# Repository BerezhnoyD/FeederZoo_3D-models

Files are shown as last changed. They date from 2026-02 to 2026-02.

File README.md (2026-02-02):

# FeederZoo_3D-models
Repository containing most of my 3d-printed models classified by their function
Contains my OpenSourceOpenField and a bunch of other stuff including the whole FeederZoo (multiple rodent feeders over the years)

Contents:
- BrainSurgery models
- FeederZoo models (lots of stuff here)
- OpenSourceLabEquipment (various models from various places)
- OpenSourceOpenField
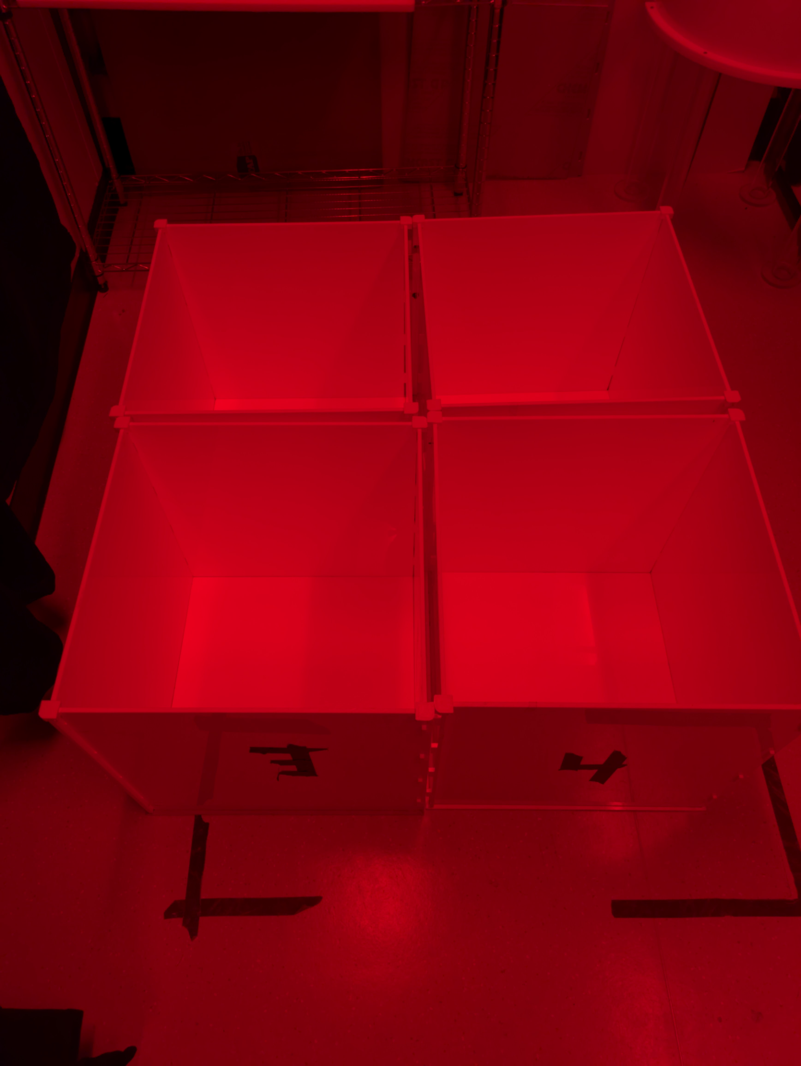
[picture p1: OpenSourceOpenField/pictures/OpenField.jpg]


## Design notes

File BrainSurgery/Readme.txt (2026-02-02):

This folder contains all the model files related
to stereotactic surgery and implants.
- Mouse headlplate files
- Holders compatible with Thorlabs poles to headfix mice with headplates/titanium bars
- Simple motorized addon for the RWD stereotax (motor housing, gear and board housing)
- Simple Cap/Shaft for Neuronexus silicon probes, tested with 32channel probes

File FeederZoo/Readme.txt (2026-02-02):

This folder contains the Whole zoo of animal feeders used
in my various behavioral projects over the years. Feel free to explore 
and modify to your needs.
- FED feeder (slightly modified pellet hopper from Markowitz lab/ eventually turned into a disc hopper for ReachOut)
- Homecage_Feeder (copied from another repository, used as an inspiration for own systems)
- ReachOut disc feeder (disc feeder used for out project with motor kinematics, see ReachOut repo or article)
- Ohanes_DIY_Linear_Servo (linear actuator turned precision pellet delivery system by my friend at VAI)
- Operant_Camera MIPT (operant camera and a feeder developed by my friends at MIPT)
- Water_delivery (syringe pump models used for my head-fixed reaching setup, see ReachOut repo)

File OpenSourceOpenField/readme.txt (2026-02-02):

This repository includes all the designs to make a module open-field box
40x40cm in size using the 5mm Acrylic Sheets.

Instructions:
For one Open field you will need to cut 5 Acrylic sheets and print 4 corners to
hold them together

1. Using the Laser Cutter (we used VLS 4.60 Laser Cutter) cut 4 side walls using 
the Illustrator files provided (Open field box-wall.ai). All walls are cut using
the same design and are hold together by the slots/spikes on the opposite side,
making all of them interchangeable. 
Use white acrylic sheets (3mm thickness) for the walls and don't remove the protective paper, 
otherwise the laser will leave the black burned marks on the surface.

2. Using the Laser Cutter cut the groves in a 5mm acryllic sheet to use it as an open-field
base. Groves are needed to hold 4 walls in place and should be at least 2-3mm deep, the deeper
the better. Provided Illustrator file (Open field box-bottom.ai) has only one grove (in grey)
as we have found that simply engraving one at a time and then rotating the sheet manually takes
much less time then engraving all. You might also want to experiment with the speed of the laser
cutter to make the grove deeper, or make some adjustments to the design

3. Using the PLA 3d printer and provided design (Open field box-corner.stl) print 4 corners to hold
the walls together. The open field can be used even without the corners due to its design,
but they add additional stability.

4. Assemble the parts in place - put the base on the floor, insert 4 walls into each other (spikes into
slots) and the base, and finish with putting 4 corners on top. The open field is ready for your experiments.
To wipe the base after the experiment you can simply lift 4 walls and then put them back in place.

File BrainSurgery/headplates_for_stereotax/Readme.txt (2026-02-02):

This folder contains all the files used for fabrication of 
titanium headplates for mouse surgeries. We printed the them using
SendCutSend service and 3mm titanium, 
but you can find another service/material of your choice.

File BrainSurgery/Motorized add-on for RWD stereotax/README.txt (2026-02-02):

Motorized add-on for RWD stereotaxic instruments by Remi-Rafael on Thingiverse: https://www.thingiverse.com/thing:7032259

Summary:
This design is an add on to motorize a RWD stereotaxic manual instrument and drive it with a servomotor. I designed it to allow slow and regular probe insertions.It adapts to the stereotaxic arm, holds with two screws and can be easily removed. The motor can be engaged or disengaged for manual control using a knob. I used 2 servo-tester modules to make a control board. The 3D parts and schematics are included.Different gears are included depending on the reduction ration you need.The servo teste i use can be found here https://www.amazon.com/GoolRC-Tester-Consistency-Helicopter-Airplane/dp/B00LTOD4F4 (and cheaper on aliexpress)

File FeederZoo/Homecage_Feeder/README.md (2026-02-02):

# **Overview**:

This system allows the user to host up to 5 mice in their home environment and automatically administer the single pellet reaching test to those animals. The system can run unsupervised and continuously for weeks at a time, allowing all 5 mice to perform an unlimited number of single pellet trials at their leisure. 

The design allows a single mouse at a time to enter the reaching tube. Upon entry, the animal’s RFID tag will be read, and if authenticated, a session will start for that animal. A session is defined as everything that happens from the time an animal enters the reaching tube to when they leave the tube. At the start of a session, the animal’s profile will be read and the task difficulty as well as the left and right preference will be automatically adjusted by moving the pellet presentation arm to the appropriate distance both away from the reaching tube and from right to left. Pellets will continue to be presented periodically until the mouse leaves the tube, at which point the session will end. Video and other data is recorded for the duration of each session. At session end, all the data for the session is saved in an organized way. We also have an auxiliary function for counting the successful rate of displaying a pellet using MobileNetV2 based on tensorflow and keras.

For further analyse, you can check the repository posted here:
https://github.com/SilasiLab/HomecageSinglePellet_Manual

# **Dependencies:**
* Ubuntu v16.04 LTS: Kernel version 4.4.19-35 or later
* Or Windows 10 is recommended, since the backend camera driver performs better that the one on linux in our experiment.
* Anaconda 3 environment, for the dependancies without a version number, it means there is no specific requirement on it. 
	* Python==3.6.10
	* pySerial==3.4	
	* numpy==1.18.1
	* OpenCV=4.1.2 (A whl file is provided under requirment folder.)
	* tkinter=8.6.8
	* matplotlib=3.1.3
	* Pillow
	* tqdm
	* tensorflow=1.10.0
	* keras=2.2.4
	* psutil
	* multiprocessing
	* subprocess
	
* Arduino IDE v1.8.5

# **Software Installation:**
1. Windows 10 is strongly recommended for a better support of camera driver. Ubuntu 16.04 LTS is alternative.
2. Install Anaconda. (https://www.anaconda.com/distribution/)
3. Install Arduino IDE v1.8.5. (https://www.arduino.cc/en/Main/Software)
	
4. Create and configure a virtual environment for installing the HomeCageSinglePellet code.
	- `conda create -n <yourenvname> python=3.6.10 anaconda`
	- `conda activate <yourenvname>`
	- `conda install -c anaconda numpy==1.18.1`
	- `conda install -c anaconda pyserial==3.4`
	- `conda install -c anaconda tk==8.6.8`
	- `conda install -c conda-forge matplotlib`
	- `conda install tqdm`
	- `conda install Pillow`
	- `conda install tensorflow==1.10.0`
	- `conda install keras==2.2.4`
	- `pip install psutil`
	- `pip install /path/to/HomeCageSinglePellet_server/requirment/opencv_python-4.1.2+contrib-cp36-cp36m-win_amd64.whl`

5. `git clone https://github.com/SilasiLab/HomeCageSinglePellet_server.git`

# **Assembly:**

The detailed assembly manual can be found here:
https://github.com/SilasiLab/HomeCageSinglePellet_server/blob/master/Homecage%20assembly%20manual.pdf

# **Usage**:
### **Running the Device**
1. Enter the virtual environment that the system was installed in by typing `conda activate <my_env>` into a terminal.

2. Optional: Use `cd` to navigate to` HomeCageSinglePellet_server/src/client/` and then run `python -B genProfiles.py`. The text prompts will walk you through entering your new animals into the system. Since the folder and the file are already inclued in this repo, this step is optional.

3. Open HomeCageSinglePellet_server/config/config.txt and set the system configuration you want.

4. Find the COM port ids for Arduino and RFID reader, using `mode` command in terminal.
(In linux: Arduino needs to be USB0 , and RFID reader needs to be USB1. You can see connected USB devices with terminal command:
ls /dev/tty* and You need to replace the COMs in main.py -> `sys_init()` function manually.) 
  
5. Open a termanal and run following command:
* `cd \your\path\to\HomeCageSinglePellet_server\src\client\`
* `conda activate YourEnvironment` replace YourEnvironment by the name of your environment.
* `python main.py COM-arduino COM-RFID` replace COM-arduino and COM-RFID by the COM ids of Arduino and RFID respectively.

6. Optional: If you have a google file stream mounted on this computer, you can choose to upload all the viedos and log files to google drive. You need firstly find out the local path to this google drive folder, in this case it is: `G:\Shared drives\SilasiLabGdrive`.
Since there could be mutiple cage running on the same computer and they can also be stored in the same google cloud folder. You can add a suffix to the project foler name by changing the root folder name from `HomeCageSinglePellet_server` to `HomeCageSinglePellet_server_id`(replace the id by your id) 
In the same folder, open another terminal and activate the virtual environment again, modify the cage ID in the script googleDriveManager.py, then run `python googleDriveManager.py \path\to\your\cloud\drive\folder`.
The videos and the log files will be stored in `your cloud drive\homecage_id_sync`.

7. You need to put in the RFID tag numbers manually into the profiles. Take mouse 1 as an instance, you need to replace the first line in `HomeCageSinglePellet_server\AnimalProfiles\MOUSE1\MOUSE1_save.txt`. If you do not know your tag number, don't worry. You can scan it on the RFID reader, it will be printed in the Terminal as `[tag number] not recognized`.

8. To test that everything is running correctly, block the IR beam breaker with something
	and scan one of the system’s test tags. If a session starts properly, it’s working. You will also be able to find out hom many pellets have been succefully displayed out of current displays we have as it is shown in the terminal too. 

9. To shut the system down cleanly; 

	- Ensure no sessions are currently running. 
	- Press the quit button on the GUI.
	- Ctrl+c out of the program running in the terminal.

# **Troubleshooting**:

* Is everything plugged in?
* Make sure you are in the correct virtual environment.
* Make sure the HomeCageSinglePellet/config/config.txt file contains the correct configuration. (If the file gets deleted it will be replaced by a default version at system start)
* Make sure there are 1 to 5 profiles in the HomeCageSinglePellet/AnimalProfiles/ directory. Ensure these profiles contain all the appropriate files and that the save.txt file for each animal contains the correct information.

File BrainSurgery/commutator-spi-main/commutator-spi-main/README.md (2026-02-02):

# Torque-free SPI Commutator

The wide-spread availability of 6 degree of freedom pose tracking using internal-measurement units
(IMUs) allows continuous monitoring of an animal's rotational state in an environment. This obviates
the need for tether torque measurements to drive an active commutator since the rotational state of
the animal is known in real-time, and the commutator can simply follow along. This commutator
supports SPI tethers i.e. any headstage that connects to the [standard 12-conductor SPI
cables](https://intantech.com/RHD_SPI_cables.html) with Omnetics connectors.

Zero-torque coaxial commutator.

This commutator functions with headstages that can provide orientation data over SPI. It can also be
used with SPI headstages without an IMU, e.g. using video-based rotation tracking since its remote
control interface is agnostic to how rotational measurements are taken.

For more information, visit the [commutator docs](https://open-ephys.github.io/commutator-docs/).

## Bill of Materials (BOM)

The following BOM pertains to the commutator's mechanical design. You can find the electronics BOM in the [commutator-controller repo](https://github.com/open-ephys/commutator-controller/tree/main/pcb/manufacturing/bom).

| Qty. | Part | Part No. | Description | Link |
| --- | --- | --- | --- | --- |
| 1	| Slip Ring Rotary Joint | Custom part from Orbex | 12-channel Slip Ring with Omnetic Connectors | - |
| 1 | NEMA 11 motor | 11HS18-0674S | 45mm length, 1.8 deg step angle, ~600mA max | [link](https://www.omc-stepperonline.com/nema-11-bipolar-1-8deg-9-5ncm-13-5oz-in-0-67a-4-6v-28x28x45mm-4-wires-11hs18-0674s) |
| 1 | 3D printed case | Custom part | 3D printed | [link](https://github.com/open-ephys/commutator-spi/tree/main/mechanical/production) |
| 1 | 3D printed motor gear | Custom part | 3D printed | [link](https://github.com/open-ephys/commutator-spi/tree/main/mechanical/production) | 
| 1 | 3D printed commutator gear | Custom part | 3D printed | [link](https://github.com/open-ephys/commutator-spi/tree/main/mechanical/production) | 
| 3 | M5 x 8mm socket head cap screws | 91290A224 | for attaching rotary joint to case | [link](https://www.mcmaster.com/91290A224) |
| 4 | M2.5 x 8mm socket head cap screws | 91290A102 | for attaching motor to case | [link](https://www.mcmaster.com/91290A102) |
| 4 | M2.5 x 8mm button head screws | 91239A756 | for attaching PCB to the case | [link](https://www.mcmaster.com/91239A756) |
| 1 | Control PCB | - | - | [link](https://github.com/open-ephys/commutators/tree/main/pcb/manufacturing/gerber) |
| 1 | eBOM | - | electrical components for assembling the PCB | [link](https://github.com/open-ephys/commutators/blob/main/pcb/manufacturing/bom/oe-commutator-controller.html) |

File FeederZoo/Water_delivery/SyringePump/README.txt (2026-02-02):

Syringe Pump by Mapleperson on Thingiverse: https://www.thingiverse.com/thing:3695610

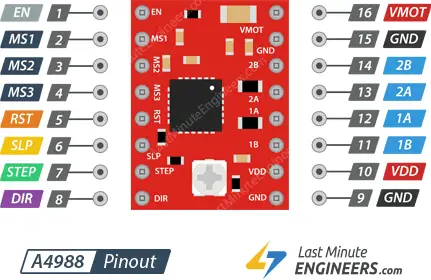
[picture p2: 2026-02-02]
BrainSurgery/Motorized-Commutator-main/Motorized-Commutator-main/Rx-PCB/Images/A4988-Stepper-Motor-Driver-Pinout.webp

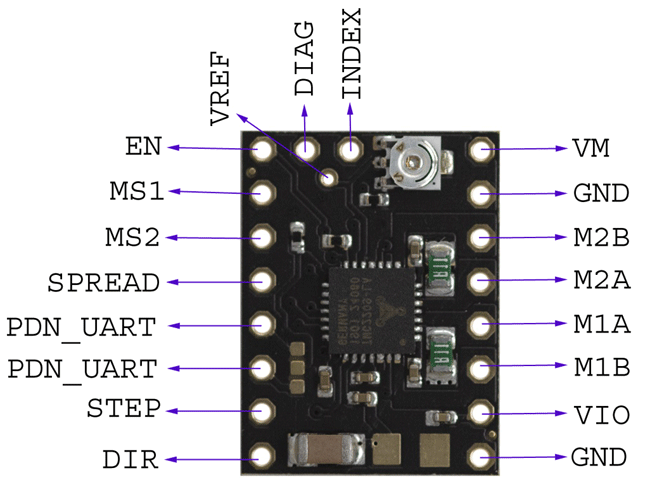
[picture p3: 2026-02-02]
BrainSurgery/Motorized-Commutator-main/Motorized-Commutator-main/Rx-PCB/Images/TMC2209-Stepper-Motor-Driver-Module-Pinout.png

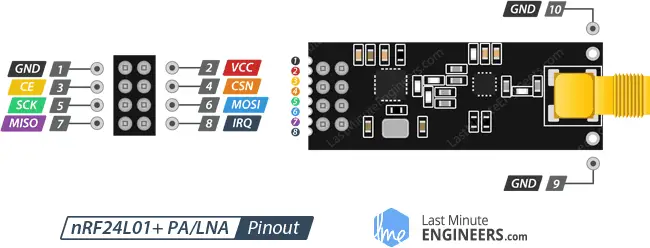
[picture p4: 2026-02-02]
BrainSurgery/Motorized-Commutator-main/Motorized-Commutator-main/Rx-PCB/Images/Pinout-nRF24L01-PA-LNA-External-Antenna-Wireless-Transceiver-Module.webp

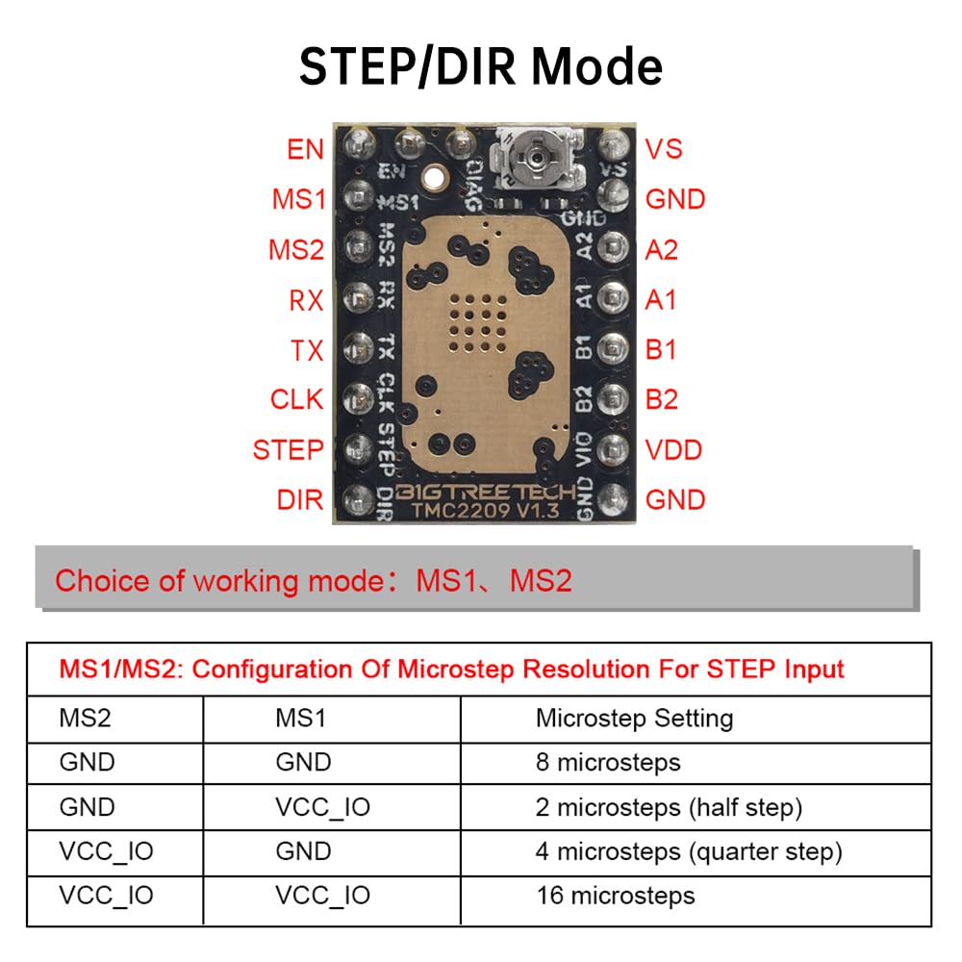
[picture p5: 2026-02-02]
BrainSurgery/Motorized-Commutator-main/Motorized-Commutator-main/Rx-PCB/Images/TMC2209_BIGTREE_Pinout.jpg

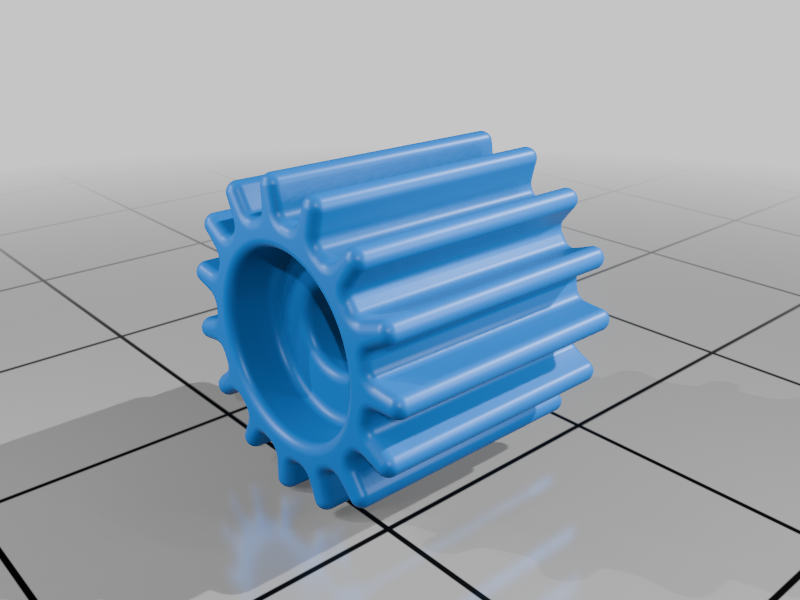
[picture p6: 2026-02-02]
BrainSurgery/Motorized add-on for RWD stereotax/images/Small_gear_1.png

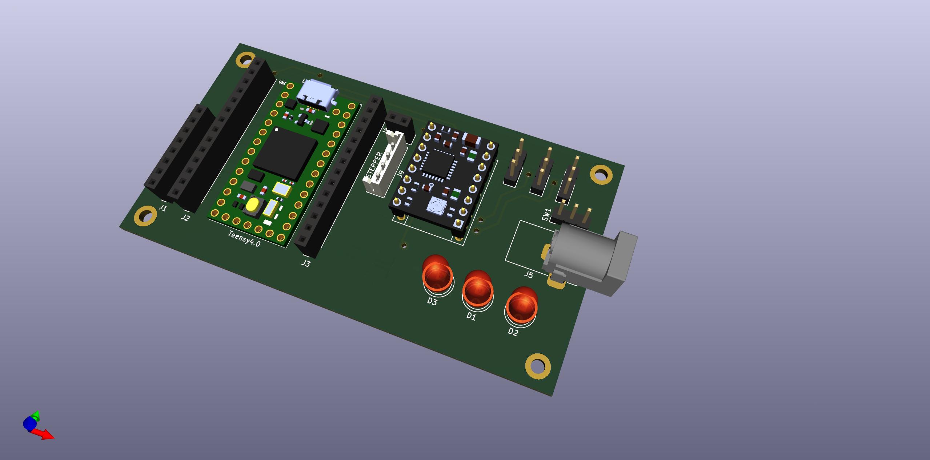
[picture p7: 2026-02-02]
BrainSurgery/Motorized-Commutator-main/Motorized-Commutator-main/Rx-PCB/Images/MC_Circuit_v2.jpg

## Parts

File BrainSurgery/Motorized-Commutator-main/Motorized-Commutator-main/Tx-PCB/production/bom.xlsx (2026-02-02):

Designator | Footprint | Quantity | Value | Manufacturer | Link
C1, C3 | 0805 | 2 | 4.7u | Digikey | https://www.digikey.com/short/3w5d9w2t
C2, C4, C5 | 0805 | 3 | 100n | Digikey | https://www.digikey.com/short/4dd80znh
C6 | 0805 | 1 | 10u | Digikey | https://www.digikey.com/short/wmr939bj
D1 | 1206 | 1 | Blue LED | Digikey | https://www.digikey.com/short/mf92djr0
D2 | 1206 | 1 | Red LED | Digikey | https://www.digikey.com/short/r8fdmfmb
J1 | PinSocket_2x04_P2.54mm_Vertical | 1 | NRF24L01 (Pin Sockets) | Digikey | https://www.digikey.com/short/vdjmc8hp | Amazon | https://a.co/d/cfL7IRG
J2 | PinSocket_1x10_P2.54mm_Vertical | 1 | Conn_01x10_Female | Digikey | https://www.digikey.com/short/pmj98dpn | Amazon | https://a.co/d/0p1lfKS
J3 | PinSocket_1x14_P2.54mm_Vertical | 1 | Conn_01x14_Female | Digikey | https://www.digikey.com/short/d7hpvht0 | Amazon | https://a.co/d/bVOCXlm
R1, R2 | 0805 | 2 | 220R | Digikey | https://www.digikey.com/short/1dt4nj9j
S1 | SW_100SP1T1B4M2QE | 1 | SW_SPDT_MODE | Digikey | https://www.digikey.com/short/8rz9r7b4
U1 | XDCR_COM-09032 | 1 | LEFT_STICK | Digikey | https://www.digikey.com/short/4ddjt05h
U2 | MODULE_DEV-15583 | 1 | Teensy4.0 (Pin Sockets) | Amazon | https://a.co/d/bVOCXlm
U3 | SOT-223-3_TabPin2 | 1 | LD1117S33TR_SOT223 | Digikey | https://www.digikey.com/short/zf93pn3w
U4 | XDCR_COM-09032 | 1 | RIGHT_STICK | Digikey | https://www.digikey.com/short/4ddjt05h
 | JUMPER |  |  | Digikey | https://www.digikey.com/short/t05tvr0v
 | Pin Headers Male |  |  | Digikey | https://www.digikey.com/short/n5mf5ppp
 | LD1117S50TR |  |  | Digikey | https://www.digikey.com/short/v05bp89n
 | Green LED |  |  | Digikey | https://www.digikey.com/short/2q5jbftb
 | 1.27mm Pin Header |  |  | Digikey | https://www.digikey.com/short/jfpnqzmq
 | 100u |  |  | Digikey | https://www.digikey.com/short/7h7q48zm
 | Barrel Jack |  |  | Digikey | https://www.digikey.com/short/df3m72bh
 | Teensy 4.0 |  |  | Digikey | https://www.digikey.com/short/wq508nbr
 | Teensy 4.0 (Headers) |  |  | Digikey | https://www.digikey.com/short/jrw35j00
 | NRF24L01 |  |  | Digikey | https://www.digikey.com/short/q3cj1zqz | Amazon | https://a.co/d/0G7uEZj
 | TMC2209 |  |  | Digikey | https://www.digikey.com/short/c970td25 | Amazon | https://a.co/d/i0fe6RV

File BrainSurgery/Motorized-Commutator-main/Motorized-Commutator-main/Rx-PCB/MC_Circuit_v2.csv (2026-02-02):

Item | Qty | Reference(s) | Value | LibPart | Footprint | Ordered or Available | Datasheet | MANUFACTURER | MAXIMUM_PACKAGE_HEIGHT | STANDARD
 |  | A1 | Pololu_Breakout_A4988 | Driver_Motor:Pololu_Breakout_A4988 | Module:Pololu_Breakout-16_15.2x20.3mm | Yes | https://www.pololu.com/product/2980/pictures
 |  | C1 | 4.7u | Device:C_Polarized_Small | Capacitor_SMD:C_0805_2012Metric_Pad1.18x1.45mm_HandSolder |  | ~
 |  | C2 | 4.7u | Device:C_Polarized_Small | Capacitor_SMD:C_0805_2012Metric_Pad1.18x1.45mm_HandSolder |  | ~
 |  | C3 | 100n | Device:C_Small | Capacitor_SMD:C_0805_2012Metric_Pad1.18x1.45mm_HandSolder | Yes | ~
 |  | C4 | 100n | Device:C_Small | Capacitor_SMD:C_0805_2012Metric_Pad1.18x1.45mm_HandSolder | Yes | ~
 |  | C5 | 100n | Device:C_Small | Capacitor_SMD:C_0805_2012Metric_Pad1.18x1.45mm_HandSolder | Yes | ~
 |  | C6 | 10u | Device:C_Polarized_Small | Capacitor_SMD:C_0805_2012Metric_Pad1.18x1.45mm_HandSolder | Yes | ~
 |  | C7 | 100u | Device:C_Polarized | Capacitor_SMD:C_0805_2012Metric_Pad1.18x1.45mm_HandSolder |  | ~
 |  | D1 | MANUAL | Device:LED | LED_THT:LED_D5.0mm | Yes | ~
 |  | D2 | AUTO | Device:LED | LED_THT:LED_D5.0mm | Yes | ~
 |  | D3 | PWR IND | Device:LED | LED_THT:LED_D5.0mm | Yes | ~
 |  | D4 | MBR0520 | Diode:MBR0520 | Diode_SMD:D_SOD-123 |  | http://www.mccsemi.com/up_pdf/MBR0520~MBR0580(SOD123).pdf
 |  | J1 | NRF24L01 | Connector:Conn_01x08_Female | Connector_PinSocket_2.54mm:PinSocket_1x08_P2.54mm_Vertical | Yes | ~
 |  | J2 | Conn_01x14_Female | Connector:Conn_01x14_Female | Connector_PinSocket_2.54mm:PinSocket_1x14_P2.54mm_Vertical |  | ~
 |  | J3 | Conn_01x14_Female | Connector:Conn_01x14_Female | Connector_PinSocket_2.54mm:PinSocket_1x14_P2.54mm_Vertical |  | ~
 |  | J4 | 3.3V TAP | Connector:Conn_01x02_Female | Connector_PinSocket_2.54mm:PinSocket_1x02_P2.54mm_Vertical | Yes | ~
 |  | J5 | Barrel_Jack_MountingPin | Connector:Barrel_Jack_Switch | Connector_BarrelJack:BarrelJack_Horizontal |  | ~
 |  | J6 | MS1 | Connector:Conn_01x03_Male | Connector_PinHeader_2.54mm:PinHeader_1x03_P2.54mm_Vertical | Yes | ~
 |  | J7 | MS2 | Connector:Conn_01x03_Male | Connector_PinHeader_2.54mm:PinHeader_1x03_P2.54mm_Vertical | Yes | ~
 |  | J8 | MS3 | Connector:Conn_01x03_Male | Connector_PinHeader_2.54mm:PinHeader_1x03_P2.54mm_Vertical | Yes | ~
 |  | J9 | STEPPER | Connector:Conn_01x04_Female | Connector_JST:JST_EH_B4B-EH-A_1x04_P2.50mm_Vertical |  | ~
 |  | R1 | 330R | Device:R | Resistor_SMD:R_0805_2012Metric_Pad1.20x1.40mm_HandSolder | Yes | ~
 |  | R2 | 330R | Device:R | Resistor_SMD:R_0805_2012Metric_Pad1.20x1.40mm_HandSolder | Yes | ~
 |  | R3 | 330R | Device:R | Resistor_SMD:R_0805_2012Metric_Pad1.20x1.40mm_HandSolder | Yes | ~
 |  | SW1 | SW_SPDT | Switch:SW_SPDT | Connector_PinHeader_2.54mm:PinHeader_1x03_P2.54mm_Vertical |  | ~
 |  | U1 | Teensy4.0 | Teensy 4.0:DEV-15583 | Teensy 4.0:MODULE_DEV-15583 |  |  | Sparkfun | 5.87mm | Manufacturer Recommendations
 |  | U2 | LD1117S50TR_SOT223 | Regulator_Linear:LD1117S50TR_SOT223 | Package_TO_SOT_SMD:SOT-223-3_TabPin2 |  | http://www.st.com/st-web-ui/static/active/en/resource/technical/document/datasheet/CD00000544.pdf
Collated Components:
Item | Qty | Reference(s) | Value | LibPart | Footprint |  | Datasheet | MANUFACTURER | MAXIMUM_PACKAGE_HEIGHT | STANDARD
1 | 1 | A1 | Pololu_Breakout_A4988 | Driver_Motor:Pololu_Breakout_A4988 | Module:Pololu_Breakout-16_15.2x20.3mm |  | https://www.pololu.com/product/2980/pictures
2 | 2 | C1, C2 | 4.7u | Device:C_Polarized_Small | Capacitor_SMD:C_0805_2012Metric_Pad1.18x1.45mm_HandSolder |  | ~
3 | 3 | C3, C4, C5 | 100n | Device:C_Small | Capacitor_SMD:C_0805_2012Metric_Pad1.18x1.45mm_HandSolder |  | ~
4 | 1 | C6 | 10u | Device:C_Polarized_Small | Capacitor_SMD:C_0805_2012Metric_Pad1.18x1.45mm_HandSolder |  | ~
5 | 1 | C7 | 100u | Device:C_Polarized | Capacitor_SMD:C_0805_2012Metric_Pad1.18x1.45mm_HandSolder |  | ~
6 | 1 | D1 | MANUAL | Device:LED | LED_THT:LED_D5.0mm |  | ~
7 | 1 | D2 | AUTO | Device:LED | LED_THT:LED_D5.0mm |  | ~
8 | 1 | D3 | PWR IND | Device:LED | LED_THT:LED_D5.0mm |  | ~
9 | 1 | D4 | MBR0520 | Diode:MBR0520 | Diode_SMD:D_SOD-123 |  | http://www.mccsemi.com/up_pdf/MBR0520~MBR0580(SOD123).pdf
10 | 1 | J1 | NRF24L01 | Connector:Conn_01x08_Female | Connector_PinSocket_2.54mm:PinSocket_1x08_P2.54mm_Vertical |  | ~
11 | 2 | J2, J3 | Conn_01x14_Female | Connector:Conn_01x14_Female | Connector_PinSocket_2.54mm:PinSocket_1x14_P2.54mm_Vertical |  | ~
12 | 1 | J4 | 3.3V TAP | Connector:Conn_01x02_Female | Connector_PinSocket_2.54mm:PinSocket_1x02_P2.54mm_Vertical |  | ~
13 | 1 | J5 | Barrel_Jack_MountingPin | Connector:Barrel_Jack_Switch | Connector_BarrelJack:BarrelJack_Horizontal |  | ~
14 | 1 | J6 | MS1 | Connector:Conn_01x03_Male | Connector_PinHeader_2.54mm:PinHeader_1x03_P2.54mm_Vertical |  | ~
15 | 1 | J7 | MS2 | Connector:Conn_01x03_Male | Connector_PinHeader_2.54mm:PinHeader_1x03_P2.54mm_Vertical |  | ~
16 | 1 | J8 | MS3 | Connector:Conn_01x03_Male | Connector_PinHeader_2.54mm:PinHeader_1x03_P2.54mm_Vertical |  | ~
17 | 1 | J9 | STEPPER | Connector:Conn_01x04_Female | Connector_JST:JST_EH_B4B-EH-A_1x04_P2.50mm_Vertical |  | ~
18 | 3 | R1, R2, R3 | 330R | Device:R | Resistor_SMD:R_0805_2012Metric_Pad1.20x1.40mm_HandSolder |  | ~
19 | 1 | SW1 | SW_SPDT | Switch:SW_SPDT | Connector_PinHeader_2.54mm:PinHeader_1x03_P2.54mm_Vertical |  | ~
20 | 1 | U1 | Teensy4.0 | Teensy 4.0:DEV-15583 | Teensy 4.0:MODULE_DEV-15583 |  |  | Sparkfun | 5.87mm | Manufacturer Recommendations
21 | 1 | U2 | LD1117S50TR_SOT223 | Regulator_Linear:LD1117S50TR_SOT223 | Package_TO_SOT_SMD:SOT-223-3_TabPin2 |  | http://www.st.com/st-web-ui/static/active/en/resource/technical/document/datasheet/CD00000544.pdf

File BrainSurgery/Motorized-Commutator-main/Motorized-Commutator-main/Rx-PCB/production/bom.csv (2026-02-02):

Designator | Footprint | Quantity | Value | LCSC Part #
_3, _2, |  | 3
A1 | Pololu_A4988 | 1 | A4988/TMC2209
C1, C2 | 0805 | 2 | 4.7u
C3, C4, C5, C8 | 0805 | 4 | 100n
C6, C9 | 0805 | 2 | 10u
C7 | 0805 | 1 | 100u
D1 | 1206 | 1 | MANUAL
D2 | 1206 | 1 | AUTO
D3 | 1206 | 1 | PWR IND
J1 | PinSocket_2x04_P2.54mm_Vertical | 1 | NRF24L01
J10 | PinHeader_2x02_P2.54mm_Vertical | 1 | Conn_02x02_Odd_Even
J2 | PinSocket_1x10_P2.54mm_Vertical | 1 | Conn_01x10_Female
J3 | PinSocket_1x14_P2.54mm_Vertical | 1 | Conn_01x14_Female
J5 | BarrelJack_Horizontal | 1 | Barrel_Jack_MountingPin
J6 | PinHeader_1x03_P2.54mm_Vertical | 1 | MS1
J7 | PinHeader_1x03_P2.54mm_Vertical | 1 | MS2
J8 | PinHeader_1x03_P2.54mm_Vertical | 1 | MS3
J9 | JST_EH_B4B-EH-A_1x04_P2.50mm_Vertical | 1 | STEPPER
R1, R2, R3 | 0805 | 3 | 220R
S1 | SW_100SP1T1B4M2QE | 1 | SW_SPDT
U1 | MODULE_DEV-15583 | 1 | Teensy4.0
U2 | SOT-223-3_TabPin2 | 1 | LD1117S50TR_SOT223
U3 | SOT-223-3_TabPin2 | 1 | LD1117S33TR_SOT223

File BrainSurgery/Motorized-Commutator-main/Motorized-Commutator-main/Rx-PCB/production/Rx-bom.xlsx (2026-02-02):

Designator | Footprint | Quantity | Value | Manufacturer
_3, _2, |  | 3
A1 | Pololu_A4988 | 1 | A4988/TMC2209 | Digikey | https://www.digikey.com/short/c970td25 | Amazon | https://a.co/d/i0fe6RV
C1, C2 | 0805 | 2 | 4.7u | Digikey | https://www.digikey.com/short/3w5d9w2t
C3, C4, C5, C8 | 0805 | 4 | 100n | Digikey | https://www.digikey.com/short/4dd80znh
C6, C9 | 0805 | 2 | 10u | Digikey | https://www.digikey.com/short/wmr939bj
C7 | 0805 | 1 | 100u | Digikey | https://www.digikey.com/short/7h7q48zm
D1 | 1206 | 1 | MANUAL | Digikey | https://www.digikey.com/short/mf92djr0
D2 | 1206 | 1 | AUTO | Digikey | https://www.digikey.com/short/r8fdmfmb
D3 | 1206 | 1 | PWR IND | Digikey | https://www.digikey.com/short/2q5jbftb
J1 | PinSocket_2x04_P2.54mm_Vertical | 1 | NRF24L01 | Digikey | https://www.digikey.com/short/vdjmc8hp | Amazon | https://a.co/d/cfL7IRG
J10 | PinHeader_2x02_P2.54mm_Vertical | 1 | Conn_02x02_Odd_Even | Digikey | https://www.digikey.com/short/094vw344
J2 | PinSocket_1x10_P2.54mm_Vertical | 1 | Conn_01x10_Female | Digikey | https://www.digikey.com/short/pmj98dpn | Amazon | https://a.co/d/0p1lfKS
J3 | PinSocket_1x14_P2.54mm_Vertical | 1 | Conn_01x14_Female | Digikey | https://www.digikey.com/short/d7hpvht0 | Amazon | https://a.co/d/bVOCXlm
J5 | BarrelJack_Horizontal | 1 | Barrel_Jack_MountingPin | Digikey | https://www.digikey.com/short/df3m72bh
J6 | PinHeader_1x03_P2.54mm_Vertical | 1 | MS1 | Digikey | https://www.digikey.com/short/n5mf5ppp
J7 | PinHeader_1x03_P2.54mm_Vertical | 1 | MS2 | Digikey | https://www.digikey.com/short/n5mf5ppp
J8 | PinHeader_1x03_P2.54mm_Vertical | 1 | MS3 | Digikey | https://www.digikey.com/short/n5mf5ppp
J9 | JST_EH_B4B-EH-A_1x04_P2.50mm_Vertical | 1 | STEPPER | Digikey | https://www.digikey.com/short/0vr4phzf
R1, R2, R3 | 0805 | 3 | 220R | Digikey | https://www.digikey.com/short/1dt4nj9j
S1 | SW_100SP1T1B4M2QE | 1 | SW_SPDT | Digikey | https://www.digikey.com/short/8rz9r7b4
U1 | MODULE_DEV-15583 | 1 | Teensy4.0 | Digikey | https://www.digikey.com/short/jrw35j00
U2 | SOT-223-3_TabPin2 | 1 | LD1117S50TR_SOT223 | Digikey | https://www.digikey.com/short/v05bp89n
U3 | SOT-223-3_TabPin2 | 1 | LD1117S33TR_SOT223 | Digikey | https://www.digikey.com/short/zf93pn3w
 | JUMPER |  |  | Digikey | https://www.digikey.com/short/t05tvr0v

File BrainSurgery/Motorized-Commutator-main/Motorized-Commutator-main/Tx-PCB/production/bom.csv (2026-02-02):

Designator | Footprint | Quantity | Value | LCSC Part #
C1, C3 | 0805 | 2 | 4.7u
C2, C4, C5 | 0805 | 3 | 100n
C6 | 0805 | 1 | 10u
D1 | 1206 | 1 | MANUAL
D2 | 1206 | 1 | AUTO
J1 | PinSocket_2x04_P2.54mm_Vertical | 1 | NRF24L01
J2 | PinSocket_1x10_P2.54mm_Vertical | 1 | Conn_01x10_Female
J3 | PinSocket_1x14_P2.54mm_Vertical | 1 | Conn_01x14_Female
R1, R2 | 0805 | 2 | 220R
S1 | SW_100SP1T1B4M2QE | 1 | SW_SPDT_MODE
U1 | XDCR_COM-09032 | 1 | LEFT_STICK
U2 | MODULE_DEV-15583 | 1 | Teensy4.0
U3 | SOT-223-3_TabPin2 | 1 | LD1117S33TR_SOT223
U4 | XDCR_COM-09032 | 1 | RIGHT_STICK

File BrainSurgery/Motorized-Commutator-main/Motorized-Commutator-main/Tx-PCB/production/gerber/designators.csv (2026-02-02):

C1:1
C2:1
C3:1
C4:1
C5:1
C6:1
D1:1
D2:1
J1:1
J2:1
J3:1
R1:1
R2:1
S1:1
U1:1
U2:1
U3:1
U4:1

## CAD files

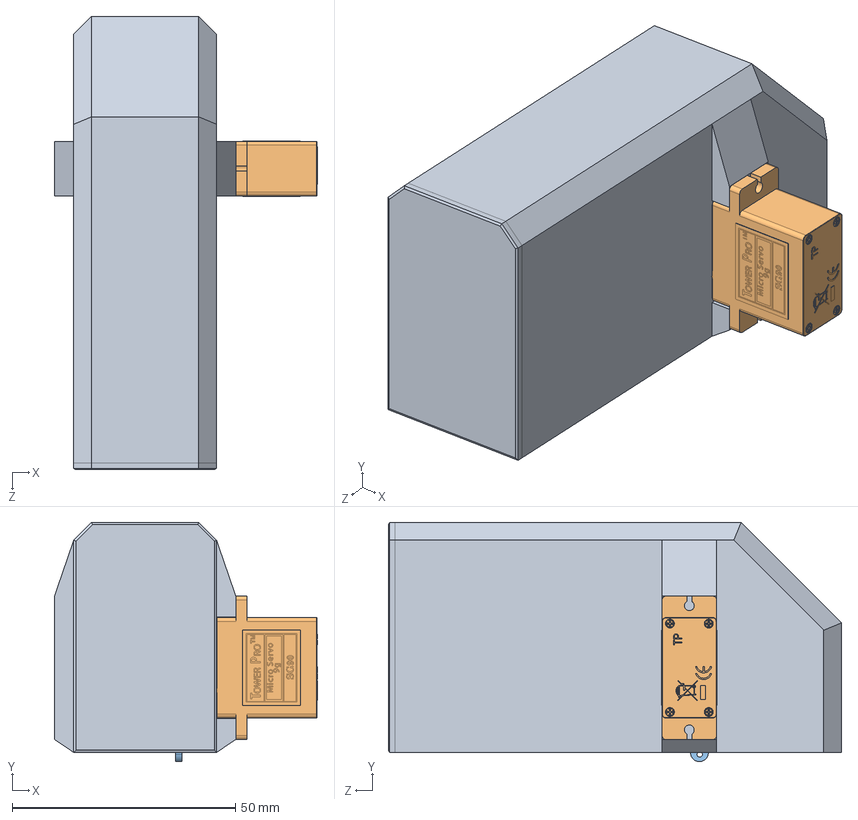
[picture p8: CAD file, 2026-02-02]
FeederZoo/Operant_Camera MIPT/Сборка1.SLDASM
58.9 x 53.6 x 101.5 mm
кормушка 2
SG90 - Micro Servo 9g - Tower Pro
SG90 - Micro Servo 9g - Tower Pro.3
вал

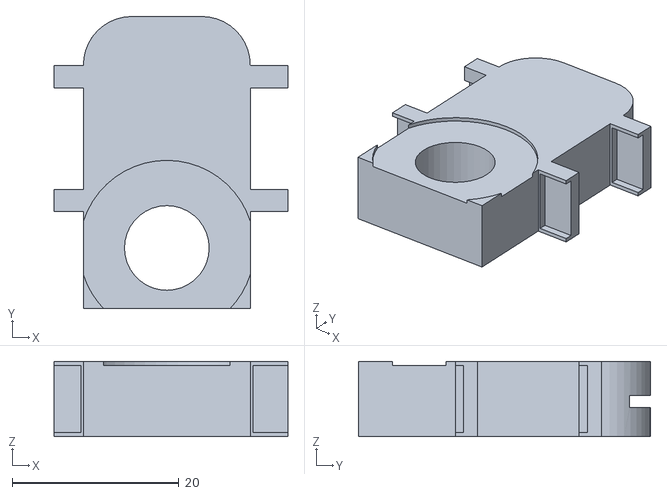
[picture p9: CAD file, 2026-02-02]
FeederZoo/Water_delivery/SyringePump/MouseParts/Mouse 2.0/Assembly Pump Mouse - M Carriage 1-2.STL
28.0 x 35.0 x 9.00

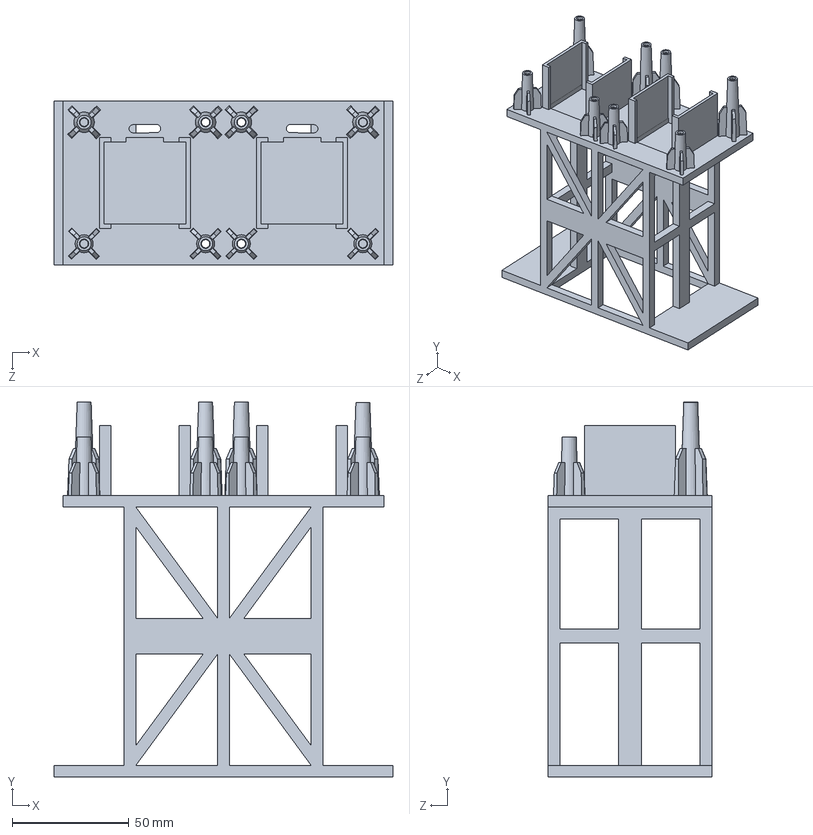
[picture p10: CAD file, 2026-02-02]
FeederZoo/Water_delivery/SyringePump/RatParts/Pho Combined Food Assembly - Skeleton - 15Matt.SLDPRT
145.0 x 160.5 x 70.0 mm

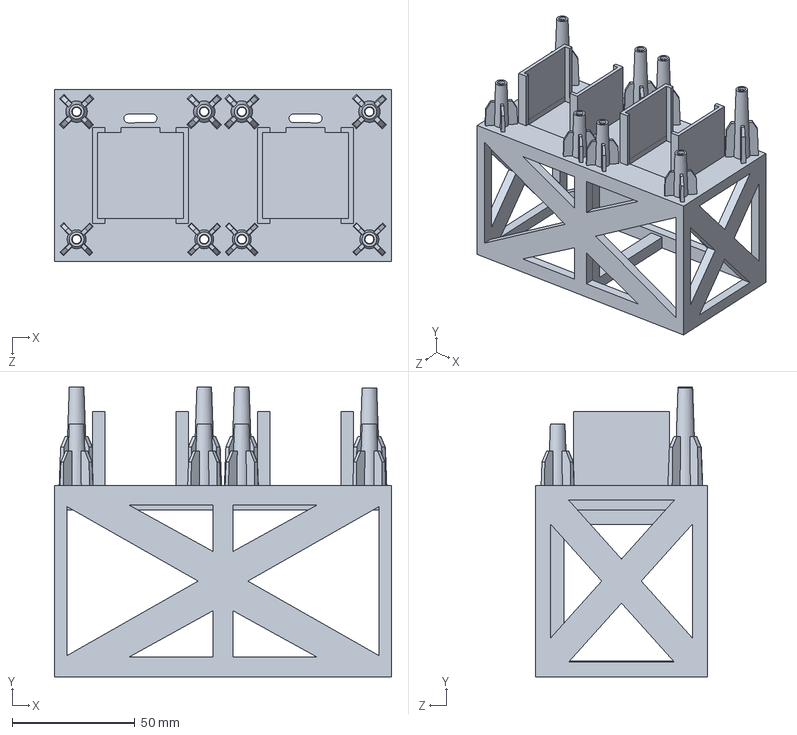
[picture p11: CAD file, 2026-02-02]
FeederZoo/Water_delivery/SyringePump/RatParts/Scaffolding/Pho Combined Food Assembly - Skeleton - 14.SLDPRT
137.3 x 118.0 x 70.0 mm

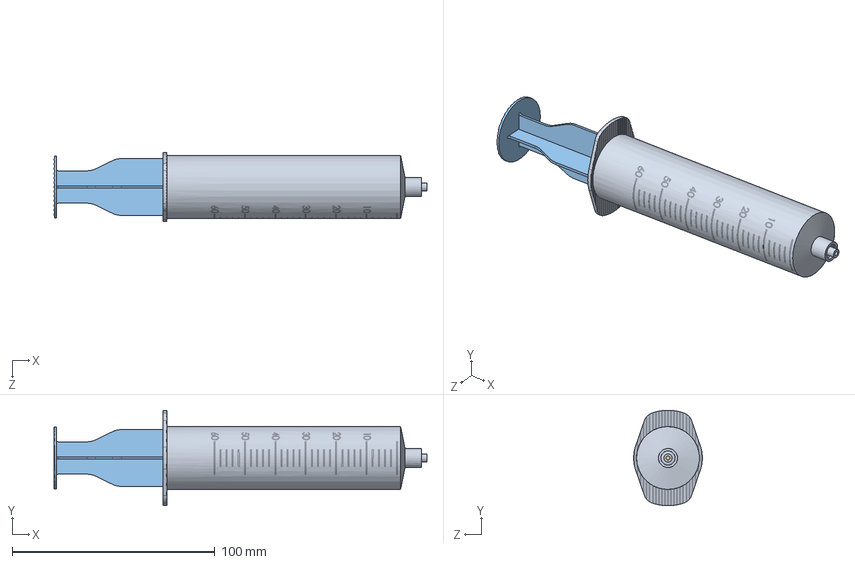
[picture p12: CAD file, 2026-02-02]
FeederZoo/Water_delivery/SyringePump/Syringe files/Syringe 60 ml.SLDASM
183.8 x 47.0 x 34.0 mm
Syringe_cylinder
Rubber tampon
Syringe_piston

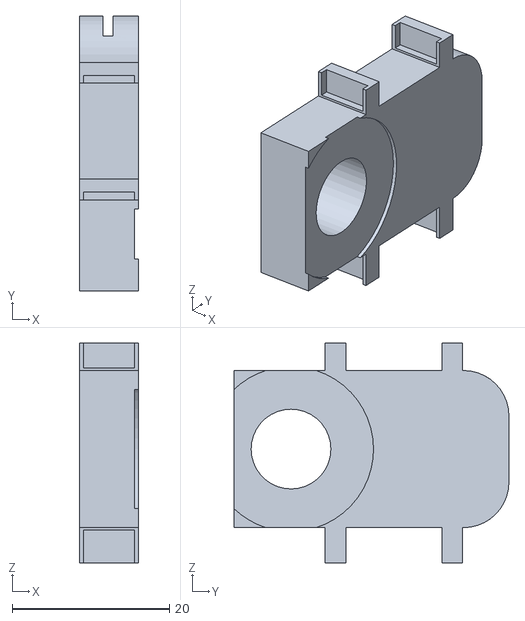
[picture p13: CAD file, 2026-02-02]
FeederZoo/Water_delivery/SyringePump/MouseParts/Mouse 2.0/Assembly Pump Mouse - M Carriage 1-1.STL
7.50 x 35.0 x 28.0

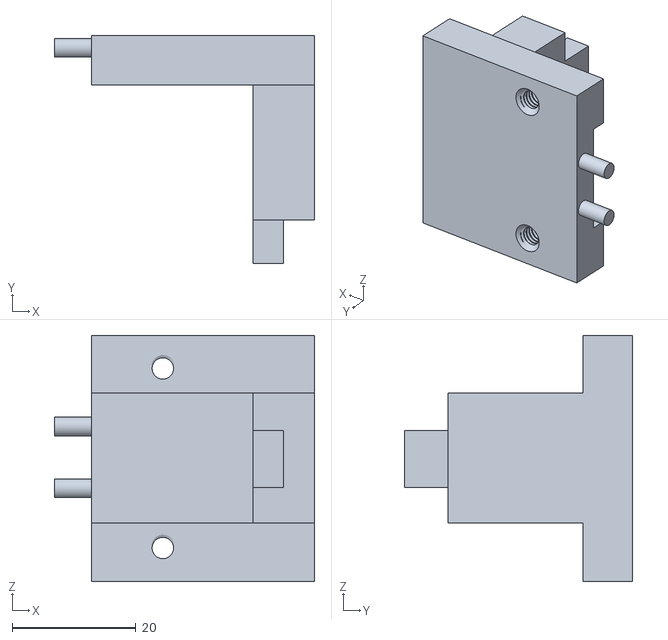
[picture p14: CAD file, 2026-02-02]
FeederZoo/Water_delivery/SyringePump/MouseParts/Mouse 2.0/Assembly Pump Mouse - M Top Lock-1.STL
42.0 x 36.9 x 39.8

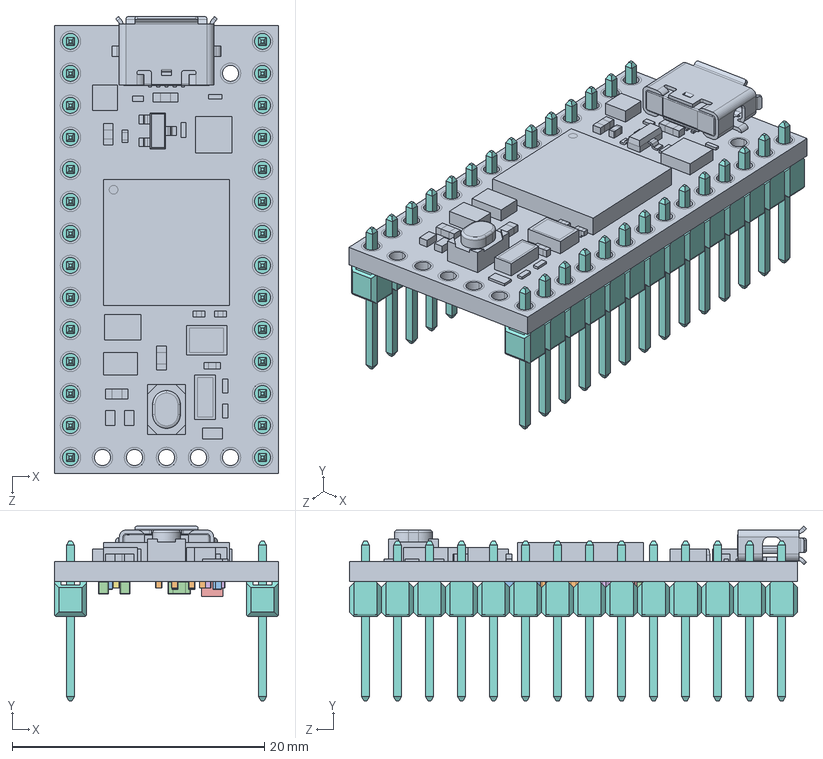
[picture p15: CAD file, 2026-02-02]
BrainSurgery/Motorized-Commutator-main/CAD/Motorized_Commutator/Teensy_40.SLDASM
17.8 x 13.9 x 36.3 mm
DEV-15583 board.step
C5-C18 (0.55mm).step
C20-C24 (0.65).step
R1-R3 (0.4inch)_1269AS-H-3R3M=P2.step
L1^DEV-15583 ASS.step
C.step x 2
C2.step
Pin Header 1x14 TH Pitch 2.54mm.stp x 2

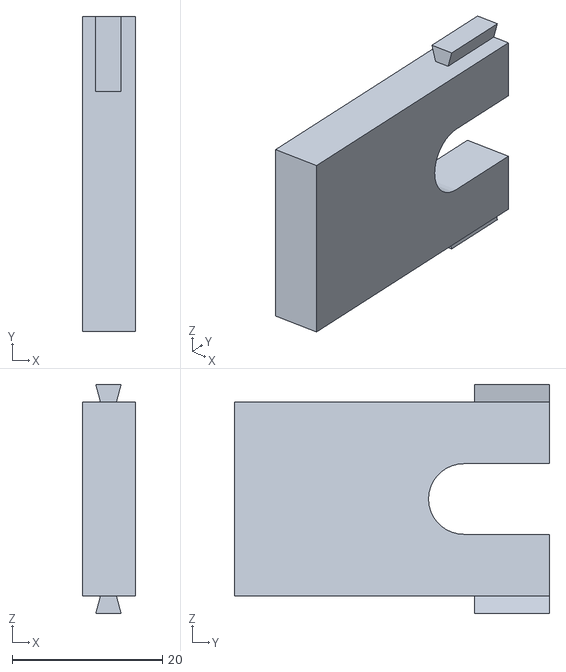
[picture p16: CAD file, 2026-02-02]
FeederZoo/Water_delivery/SyringePump/MouseParts/Mouse 2.0/Assembly Pump Mouse - M Front Face 1-1.STL
7.00 x 42.0 x 30.5

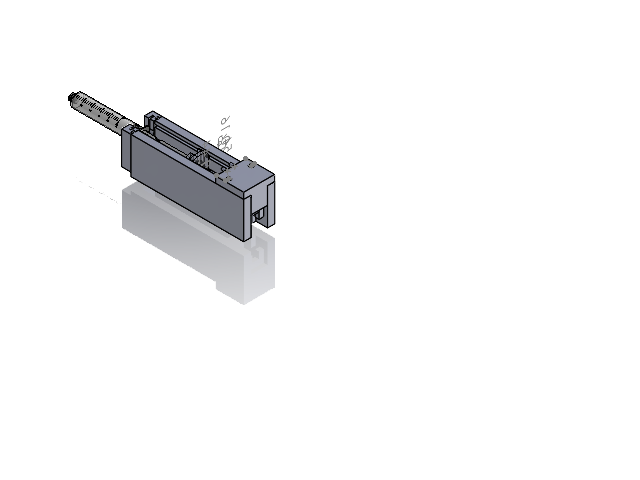
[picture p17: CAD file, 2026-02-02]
FeederZoo/Water_delivery/SyringePump/MouseParts/Assembly Pump Mouse.SLDASM
Syringe_cylinder_10ml
Rubber tampon_10ml
Syringe_piston_10ml
M Middle Face 1
M BackSideRail 1
M Carriage 1
Example actuator 100
M Top Lock

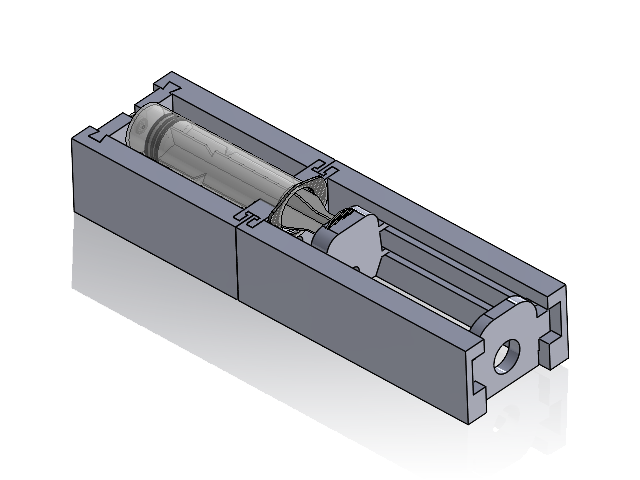
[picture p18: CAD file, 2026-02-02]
FeederZoo/Water_delivery/SyringePump/RatParts/RBB Syringe Design 0/Assem1.SLDASM
FrontFace
BackFace
MiddleFace
Carriage
BackSideRailL
BackSideRailR
Rubber tampon
Syringe_cylinder
Syringe_piston
FrontSideRailR
FrontSideRailL

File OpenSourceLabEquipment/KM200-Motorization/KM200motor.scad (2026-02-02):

use <24byj48.scad>

stepper_spacing=71.5; // from the mount corner
bracket_w=115;
bracket_offset=20;
bracket_t=15;
bracket_w_inner=8;
base_w=15;
n_w=7.2;
n_z=2.5;
screw_w=4.5;
module screw_nut_uncut(nut_depth, nut_length,nut_thick) {
	translate([0,0,-nut_length])
	cylinder(h=nut_length,d=screw_w*2,center=false,$fn=res);
	cylinder(h=nut_length,d=screw_w,center=false,$fn=res);
	translate([0,n_w/2,nut_depth+nut_thick/2-0.01])
	cube(size=[n_w,n_w*2,nut_thick], center=true);
}

module steppers(){
	translate([-stepper_spacing,9,-16])
	rotate(a=[0,0,180]){
		stepper_mounted(n_l=45,n_rot1=0,n_rot2=-0,n_d=20,screw=0, res=30);
		cylinder(h=80,d=28,center=false,$fn=res);
	}
	translate([-9,stepper_spacing,-16])
	rotate(a=[0,0,-90]){
		stepper_mounted(n_l=45,n_rot1=0,n_rot2=0,n_d=20,screw=0, res=30);
		cylinder(h=80,d=28,center=false,$fn=res);
	}
}

module lens(){
	translate([-40,40,0])
	cylinder(h=50,r=25,center=true,$fn=res);
}

module bracket(){
	difference(){
		union(){
			translate([-bracket_w/2+bracket_offset,bracket_w/2-bracket_offset,bracket_t/2])
			cube(size=[bracket_w,bracket_w,bracket_t], center=true);
			translate([-bracket_w/2+bracket_offset,-bracket_offset/2,bracket_offset])
			cube(size=[bracket_w,bracket_offset,base_w+bracket_t], center=true);
		}
		translate([-bracket_w+(bracket_w-bracket_w_inner)/2,bracket_w-(bracket_w-bracket_w_inner)/2,bracket_t/2])
		difference(){		
			cube(size=[bracket_w-bracket_w_inner,bracket_w-bracket_w_inner,bracket_t+1], center=true);
			difference(){
				translate([(bracket_w-bracket_w_inner)/4,-(bracket_w-bracket_w_inner)/4,0])
				cube(size=[(bracket_w-bracket_w_inner)/2,(bracket_w-bracket_w_inner)/2,bracket_t+1], center=true);
				cylinder(h=50,r=(bracket_w-bracket_w_inner)/2,center=true,$fn=res);
			}
		}
		//lens();
	}
}

module screws(){
	translate([0,-5,21])
	rotate(a=[90,0,0]){
		//KM200 mounting
		translate([-30,0,0])
		screw_nut_uncut(3, 45,n_z);
		translate([-40,0,0])
		screw_nut_uncut(3, 45,n_z);
		translate([-54,0,0])
		screw_nut_uncut(3, 45,n_z);
		//mounting holes
		translate([-(40-50),0,0])
		screw_nut_uncut(3, 45,n_z);
		translate([-(40+50),0,0])
		screw_nut_uncut(3, 45,n_z);
	}
}

//lens();

difference(){
	bracket();
	screws();
	steppers();
}

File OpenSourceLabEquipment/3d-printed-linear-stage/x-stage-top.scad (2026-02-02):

M3 = 1.65;
M3F = 1.8;
M3H = 3.1;
LGR = 1.2;

TXB = 10;
TYB = 10;

module top_plate(){
	difference(){
		cube(size=[35,35,3], center=true);

		translate([TXB,TYB,0]) cylinder(r=M3, h=10, center=true);
		translate([-TXB,-TYB,0]) cylinder(r=M3, h=10, center=true);
		translate([TXB,-TYB,0]) cylinder(r=M3, h=10, center=true);
		translate([-TXB,TYB,0]) cylinder(r=M3, h=10, center=true);

		cylinder(r=M3, h=10, center=true);
	}
}

module side(){
	difference(){
		cube(size=[35,4,9], center=true);

		translate([13,0,1.5]) rotate([90,30,0]) cylinder(r=LGR, h=50, $fn=6, center=true);
		translate([-13,0,1.5]) rotate([90,30,0]) cylinder(r=LGR, h=50, $fn=6, center=true);

		translate([0,0,1.5]) rotate([90,30,0]) cylinder(r=M3F, h=50, $fn=12, center=true);
		translate([0,3.5,1.5]) rotate([90,0,0]) cylinder(r=M3H, h=5, $fn=6, center=true);

	}
}

union(){
	top_plate();
	translate([0,4,3.5]) side();
	translate([0,-4,3.5]) rotate([0,0,180]) side();

}

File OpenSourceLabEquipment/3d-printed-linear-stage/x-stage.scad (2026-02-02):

M3 = 1.65;
M3F = 1.8;
M3H = 3.5;
LGR = 1.2;

TYB = 10;
TXB = 10;

module foundation(){
	difference(){
		cube(size=[35,35,3], center=true);

		translate([TXB,TYB,0]) cylinder(r=M3, h=10, center=true);
		translate([-TXB,-TYB,0]) cylinder(r=M3, h=10, center=true);
		translate([TXB,-TYB,0]) cylinder(r=M3, h=10, center=true);
		translate([-TXB,TYB,0]) cylinder(r=M3, h=10, center=true);

		translate([TXB,TYB,1.5]) cylinder(r=M3H, h=3, center=true);
		translate([-TXB,-TYB,1.5]) cylinder(r=M3H, h=3, center=true);
		translate([TXB,-TYB,1.5]) cylinder(r=M3H, h=3, center=true);
		translate([-TXB,TYB,1.5]) cylinder(r=M3H, h=3, center=true);

		cylinder(r=M3, h=10, center=true);
		translate([0,0,1.5]) cylinder(r=3.5, h=3, center=true);

	}
}

module side(){
	difference(){
		cube(size=[35,4,9], center=true);

		translate([13,0,2]) rotate([90,30,0]) cylinder(r=LGR, h=50, $fn=6, center=true);
		translate([-13,0,2]) rotate([90,30,0]) cylinder(r=LGR, h=50, $fn=6, center=true);

		translate([0,0,2]) rotate([90,30,0]) cylinder(r=M3F, h=50, $fn=12, center=true);
	}
}

union(){
	foundation();
	translate([0,15.5,3]) side();
	translate([0,-15.5,3]) side();

}

// +1.5 
// -5.5 + 3 = -2.5
// -2.5 + 11 = 8.5
// -1.5 + 11 = 9.5
//  9.5 - 1.5 = 8
//  9.5 / 2 = 4.75

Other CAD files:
BrainSurgery/Motorized-Commutator-main/CAD/Line_Maze_Gantry/Commutator-M3-Nuts.SLDASM
BrainSurgery/Motorized-Commutator-main/CAD/Line_Maze_Gantry/M5-Nuts-Comm.SLDASM
BrainSurgery/Motorized-Commutator-main/Motorized-Commutator-main/CAD/Line_Maze_Gantry/M5-Nuts-Z.SLDASM
BrainSurgery/Motorized-Commutator-main/Motorized-Commutator-main/CAD/Motorized_Commutator/Commutator-M3-Nuts.SLDASM
BrainSurgery/Motorized-Commutator-main/CAD/Motorized_Commutator/Commutator-M3-Nuts.SLDASM
BrainSurgery/Motorized-Commutator-main/Motorized-Commutator-main/CAD/Line_Maze_Gantry/IB - Vslot Actuator.SLDASM
OpenSourceLabEquipment/LensAdapter/LensAdapter.scad
BrainSurgery/Motorized add-on for Kopf stereotaxic instruments - 7128061/Grand Crift.stl
BrainSurgery/Motorized add-on for Kopf stereotaxic instruments - 7128061/Holder_p11.STL
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

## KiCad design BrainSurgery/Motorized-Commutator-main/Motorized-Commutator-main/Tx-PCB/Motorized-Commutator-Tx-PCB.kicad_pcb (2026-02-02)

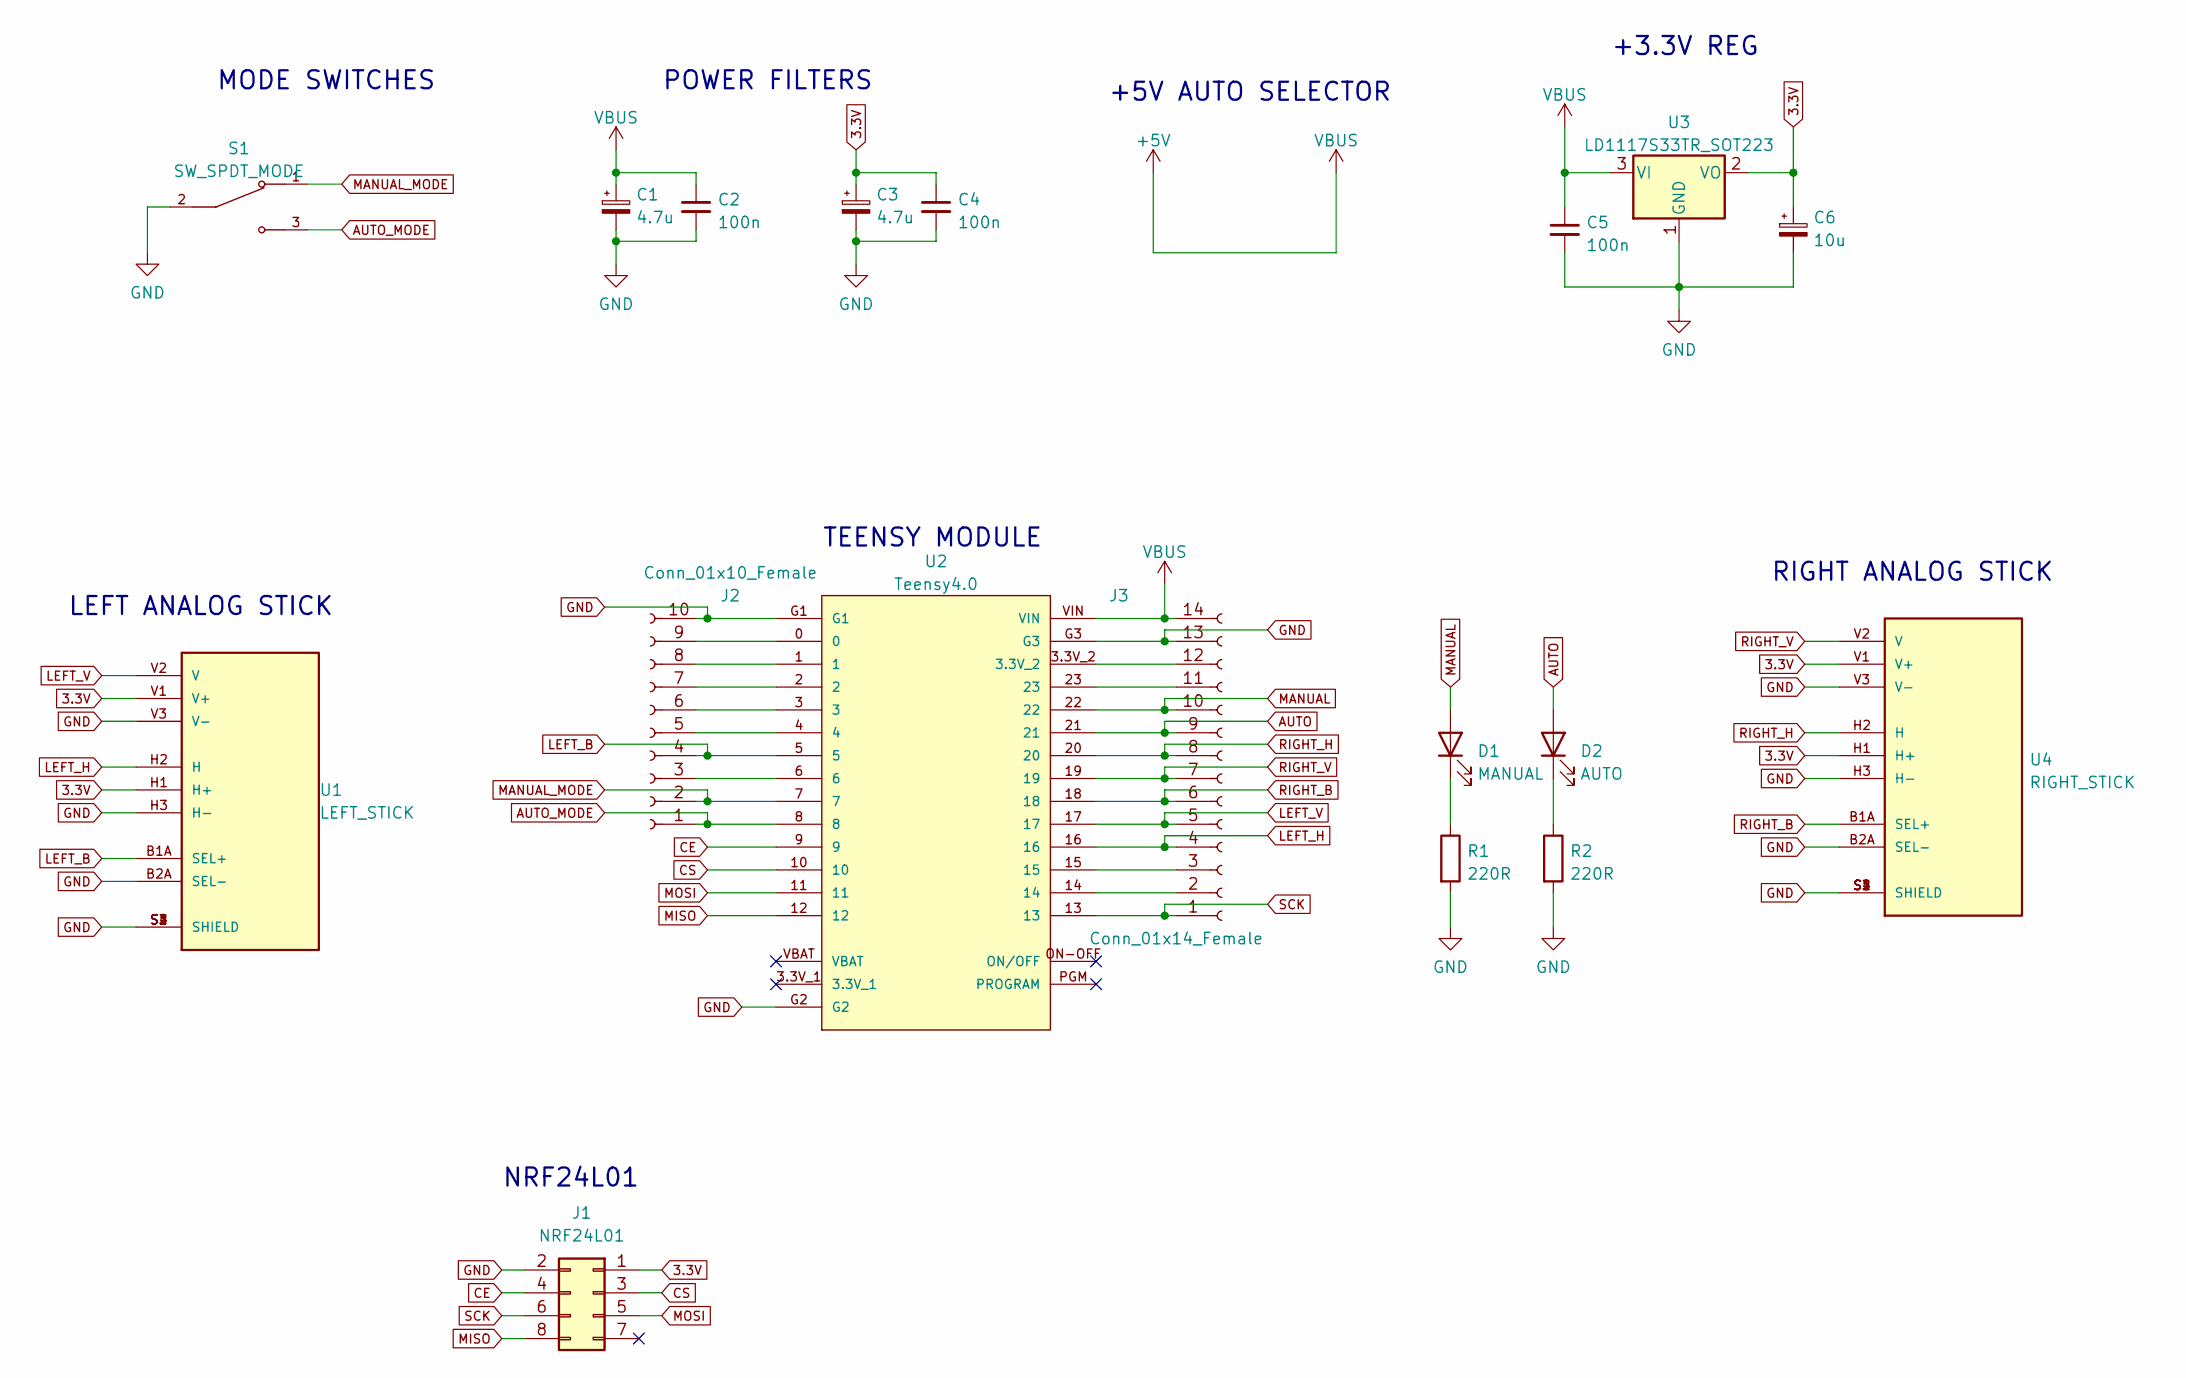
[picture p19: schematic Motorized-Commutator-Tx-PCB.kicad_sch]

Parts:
C1, C3: 4.7u; C_0805_2012Metric_Pad1.18x1.45mm_HandSolder
C2, C4, C5: 100n; C_0805_2012Metric_Pad1.18x1.45mm_HandSolder
C6: 10u; C_0805_2012Metric_Pad1.18x1.45mm_HandSolder
D1: MANUAL; LED_1206_3216Metric_Pad1.42x1.75mm_HandSolder
D2: AUTO; LED_1206_3216Metric_Pad1.42x1.75mm_HandSolder
J1: NRF24L01; PinSocket_2x04_P2.54mm_Vertical
J2: Conn_01x10_Female; PinSocket_1x10_P2.54mm_Vertical
J3: Conn_01x14_Female; PinSocket_1x14_P2.54mm_Vertical
R1, R2: 220R; R_0805_2012Metric_Pad1.20x1.40mm_HandSolder
S1: SW_SPDT_MODE; SW_100SP1T1B4M2QE; PARTREV E
U1: LEFT_STICK; XDCR_COM-09032; PARTREV N/A
U2: Teensy4.0; MODULE_DEV-15583
U3: LD1117S33TR_SOT223; SOT-223-3_TabPin2
U4: RIGHT_STICK; XDCR_COM-09032; PARTREV N/A

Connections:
3.3V: C3.1, C4.1, C6.1, J1.1, U1.H1 (H+), U1.V1 (V+), U3.2 (VO), U4.H1 (H+), U4.V1 (V+)
+5V: C1.1, C2.1, C5.1, J3.14, U2.VIN, U3.3 (VI)
AUTO: D2.2 (A), J3.9, U2.21
AUTO_MODE: J2.1, S1.3, U2.8
CE: J1.4, U2.9
CS: J1.3, U2.10
GND: C1.2, C2.2, C3.2, C4.2, C5.2, C6.2, J1.2, J2.10, J3.13, R1.2, R2.2, S1.2, U1.B2A (SEL-), U1.H3 (H-), U1.S1 (SHIELD), U1.S2 (SHIELD), U1.S3 (SHIELD), U1.S4 (SHIELD), U1.V3 (V-), U2.G1, U2.G2, U2.G3, U3.1 (GND), U4.B2A (SEL-), U4.H3 (H-), U4.S1 (SHIELD), U4.S2 (SHIELD), U4.S3 (SHIELD), U4.S4 (SHIELD), U4.V3 (V-)
LEFT_B: J2.4, U1.B1A (SEL+), U2.5
LEFT_H: J3.4, U1.H2 (H), U2.16
LEFT_V: J3.5, U1.V2 (V), U2.17
MANUAL: D1.2 (A), J3.10, U2.22
MANUAL_MODE: J2.2, S1.1, U2.7
MISO: J1.8, U2.12
MOSI: J1.5, U2.11
unnamed: D1.1 (K), R1.1
unnamed: D2.1 (K), R2.1
unnamed: J2.3, U2.6
unnamed: J2.5, U2.4
unnamed: J2.6, U2.3
unnamed: J2.7, U2.2
unnamed: J2.8, U2.1
unnamed: J2.9, U2.0
unnamed: J3.2, U2.14
unnamed: J3.3, U2.15
unnamed: J3.11, U2.23
unnamed: J3.12, U2.3.3V_2
RIGHT_B: J3.6, U2.18, U4.B1A (SEL+)
RIGHT_H: J3.8, U2.20, U4.H2 (H)
RIGHT_V: J3.7, U2.19, U4.V2 (V)
SCK: J1.6, J3.1, U2.13

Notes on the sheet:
POWER FILTERS
+5V AUTO SELECTOR
LEFT ANALOG STICK
NRF24L01
TEENSY MODULE
RIGHT ANALOG STICK
+3.3V REG
MODE SWITCHES

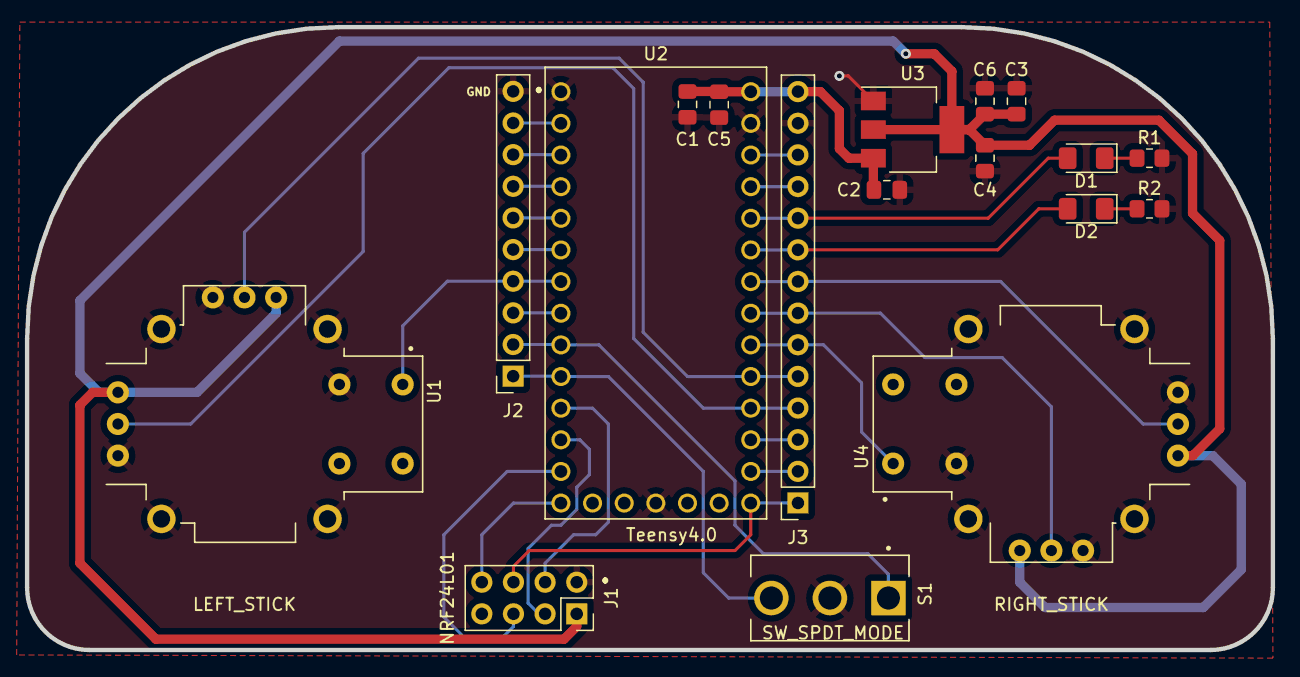
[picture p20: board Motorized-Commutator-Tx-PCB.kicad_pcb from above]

Board: 2 copper layers, 100.0 x 50.0 mm, 18 parts (0 on the bottom side), 30 nets.

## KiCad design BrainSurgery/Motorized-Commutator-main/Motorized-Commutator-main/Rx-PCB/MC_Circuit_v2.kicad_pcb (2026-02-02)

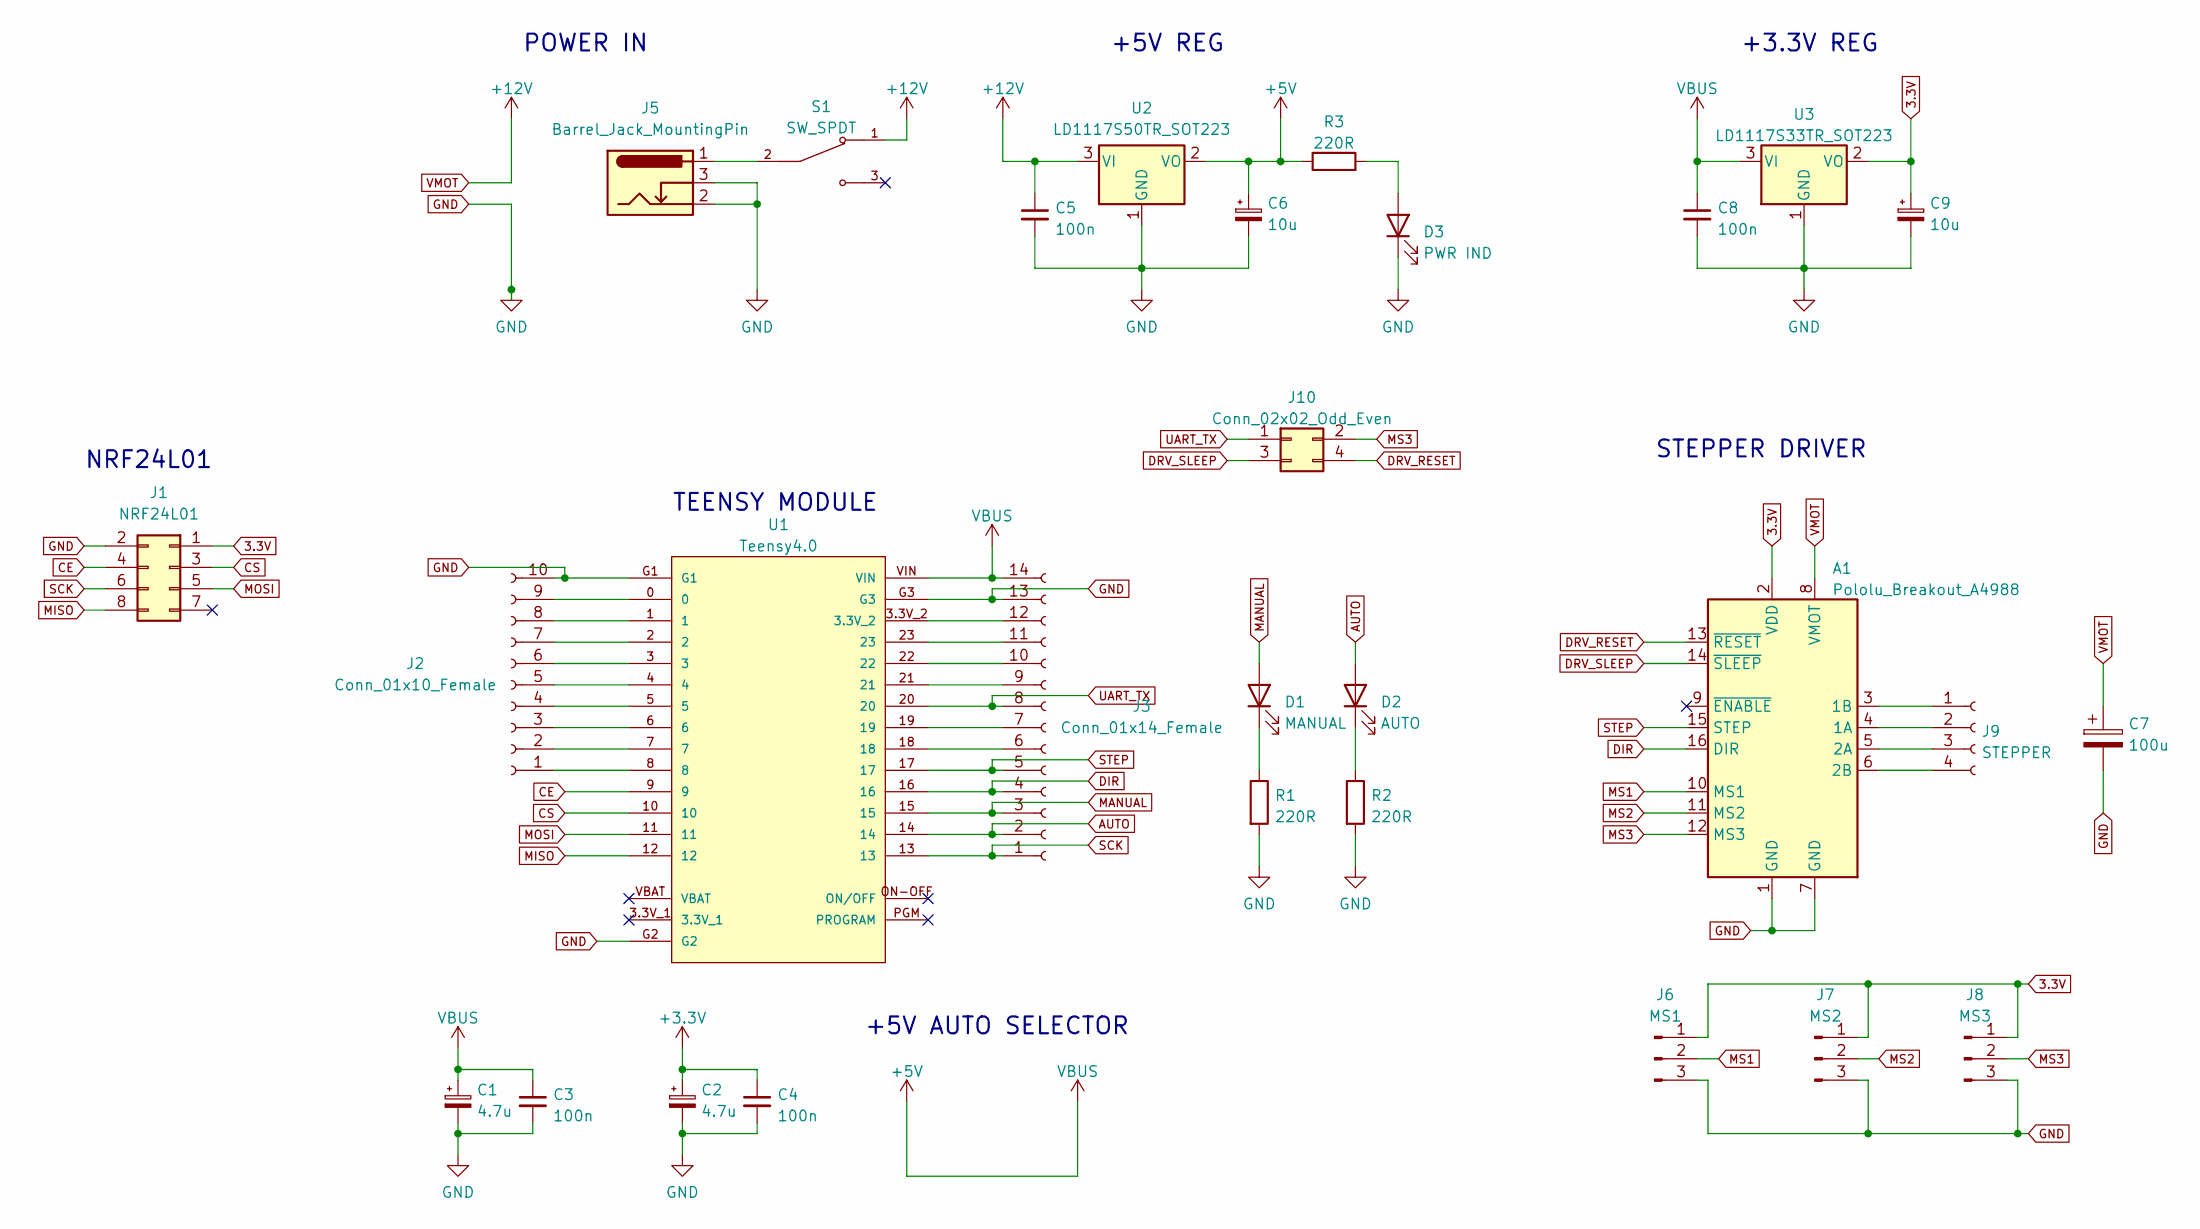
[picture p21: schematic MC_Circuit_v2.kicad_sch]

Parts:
A1: Pololu_Breakout_A4988; Pololu_Breakout-16_15.2x20.3mm
C1, C2: 4.7u; C_0805_2012Metric_Pad1.18x1.45mm_HandSolder
C3, C4, C5, C8: 100n; C_0805_2012Metric_Pad1.18x1.45mm_HandSolder
C6, C9: 10u; C_0805_2012Metric_Pad1.18x1.45mm_HandSolder
C7: 100u; C_0805_2012Metric_Pad1.18x1.45mm_HandSolder
D1: MANUAL; LED_1206_3216Metric_Pad1.42x1.75mm_HandSolder
D2: AUTO; LED_1206_3216Metric_Pad1.42x1.75mm_HandSolder
D3: PWR IND; LED_1206_3216Metric_Pad1.42x1.75mm_HandSolder
J1: NRF24L01; PinSocket_2x04_P2.54mm_Vertical
J2: Conn_01x10_Female; PinSocket_1x10_P2.54mm_Vertical
J3: Conn_01x14_Female; PinSocket_1x14_P2.54mm_Vertical
J5: Barrel_Jack_MountingPin; BarrelJack_Horizontal
J6: MS1; PinHeader_1x03_P2.54mm_Vertical
J7: MS2; PinHeader_1x03_P2.54mm_Vertical
J8: MS3; PinHeader_1x03_P2.54mm_Vertical
J9: STEPPER; JST_EH_B4B-EH-A_1x04_P2.50mm_Vertical
J10: Conn_02x02_Odd_Even; PinHeader_2x02_P2.54mm_Vertical
R1, R2, R3: 220R; R_0805_2012Metric_Pad1.20x1.40mm_HandSolder
S1: SW_SPDT; SW_100SP1T1B4M2QE; PARTREV E
U1: Teensy4.0; MODULE_DEV-15583
U2: LD1117S50TR_SOT223; SOT-223-3_TabPin2
U3: LD1117S33TR_SOT223; SOT-223-3_TabPin2

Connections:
3.3V: A1.2 (VDD), C9.1, J1.1, J6.1, J7.1, J8.1, U3.2 (VO)
+3V3: C2.1, C4.1
+5V: C1.1, C3.1, C6.1, C8.1, J3.14, R3.1, U1.VIN, U2.2 (VO), U3.3 (VI)
AUTO: D2.2 (A), J3.2, U1.14
CE: J1.4, U1.9
CS: J1.3, U1.10
DIR: A1.16 (DIR), J3.4, U1.16
DRV_RESET: A1.13 (~RESET), J10.4
DRV_SLEEP: A1.14 (~SLEEP), J10.3
GND: A1.1 (GND), A1.7 (GND), C1.2, C2.2, C3.2, C4.2, C5.2, C6.2, C7.2, C8.2, C9.2, D3.1 (K), J1.2, J2.10, J3.13, J5.2, J5.3, J6.3, J7.3, J8.3, R1.2, R2.2, U1.G1, U1.G2, U1.G3, U2.1 (GND), U3.1 (GND)
MANUAL: D1.2 (A), J3.3, U1.15
MISO: J1.8, U1.12
MOSI: J1.5, U1.11
MS1: A1.10 (MS1), J6.2
MS2: A1.11 (MS2), J7.2
MS3: A1.12 (MS3), J8.2, J10.2
unnamed: A1.3 (1B), J9.1
unnamed: A1.4 (1A), J9.2
unnamed: A1.5 (2A), J9.3
unnamed: A1.6 (2B), J9.4
unnamed: D1.1 (K), R1.1
unnamed: D2.1 (K), R2.1
unnamed: D3.2 (A), R3.2
unnamed: J2.1, U1.8
unnamed: J2.2, U1.7
unnamed: J2.3, U1.6
unnamed: J2.4, U1.5
unnamed: J2.5, U1.4
unnamed: J2.6, U1.3
unnamed: J2.7, U1.2
unnamed: J2.8, U1.1
unnamed: J2.9, U1.0
unnamed: J3.6, U1.18
unnamed: J3.7, U1.19
unnamed: J3.9, U1.21
unnamed: J3.10, U1.22
unnamed: J3.11, U1.23
unnamed: J3.12, U1.3.3V_2
unnamed: J5.1, S1.2
SCK: J1.6, J3.1, U1.13
STEP: A1.15 (STEP), J3.5, U1.17
UART_TX: J3.8, J10.1, U1.20
VMOT: A1.8 (VMOT), C5.1, C7.1, S1.1, U2.3 (VI)

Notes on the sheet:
+3.3V REG
POWER IN
TEENSY MODULE
STEPPER DRIVER
+5V REG
+5V AUTO SELECTOR
NRF24L01

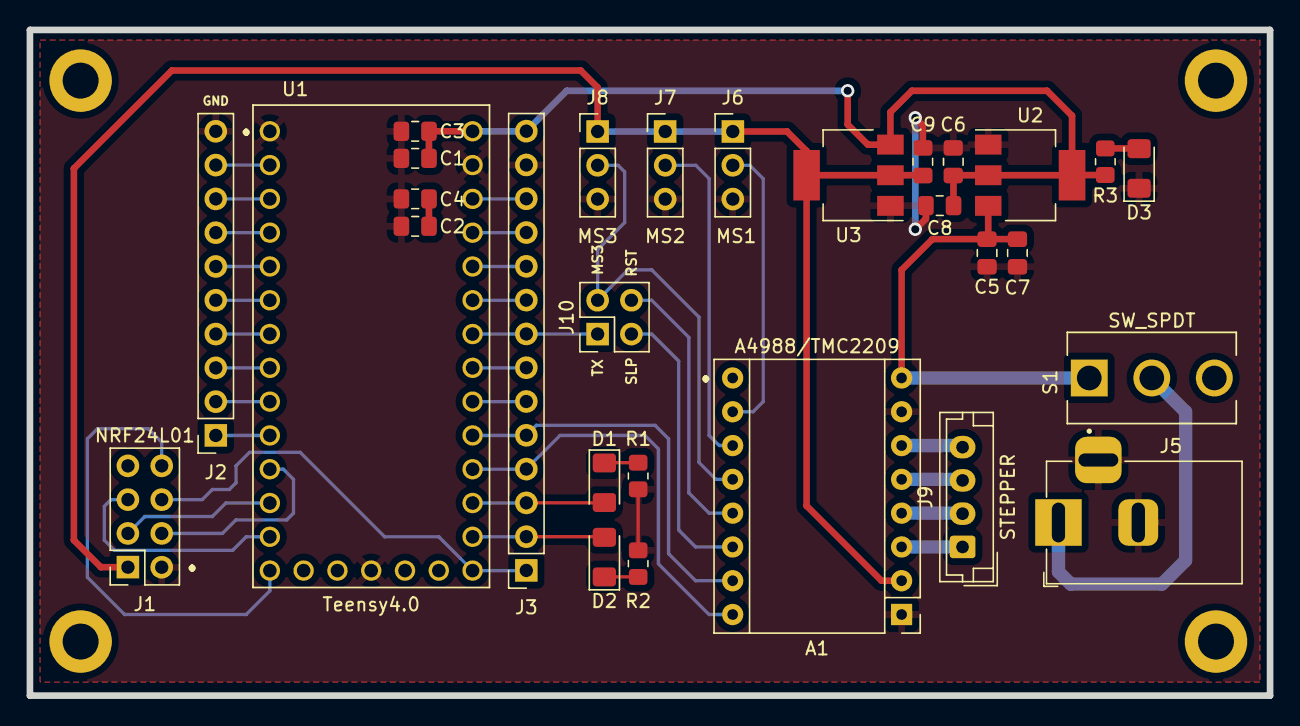
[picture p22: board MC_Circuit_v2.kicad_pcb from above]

Board: 2 copper layers, 93.2 x 50.0 mm, 29 parts (0 on the bottom side), 43 nets.
